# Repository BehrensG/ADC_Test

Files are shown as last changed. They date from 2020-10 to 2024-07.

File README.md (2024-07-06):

<h1> ADC_Test </h1>

PCB design to test the multislope ADC concept created by Jaromir Sukuba (https://github.com/jaromir-sukuba).

<h2> Design </h2>

The project features a 4-layer PCB designed in the Eurocard 3U format. The PCB operates on a 24V DC power supply. Communication is handled via Ethernet, utilizing a RAW TCP protocol with SCPI command format.
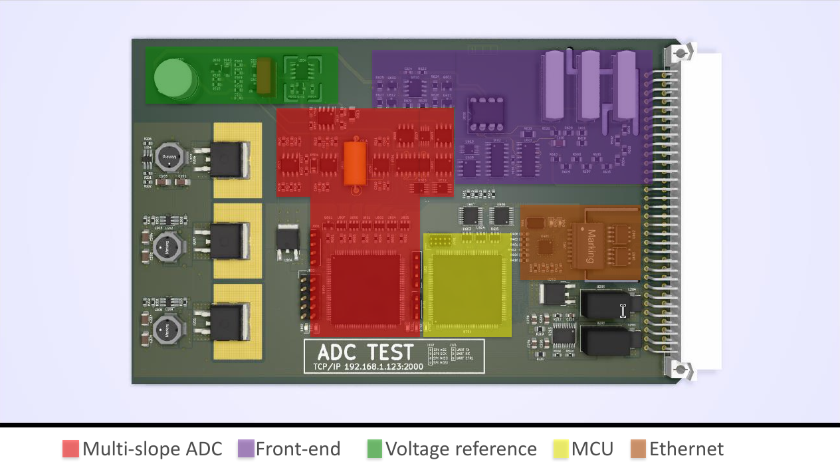
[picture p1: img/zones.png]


Key components include:
<ul>
    <li> <b>MCU</b>: STM32F765ZGT running FreeRTOS, developed with STM32CubeIDE.</li>
    <li> <b>FPGA</b>: ICE40HX4K-TQ144, with logic synthesis performed using IceStorm, and programmed in Verilog.</li>
    <li> <b>ADC</b> : Max voltage +/- 12V DC. 
            NPLC (Number of Power Line Cycles): 1, 2, 5,10 and 100.</li>
</ul>
The analog front end supports three bipolar ranges: 1V, 10V, and 100V DC.

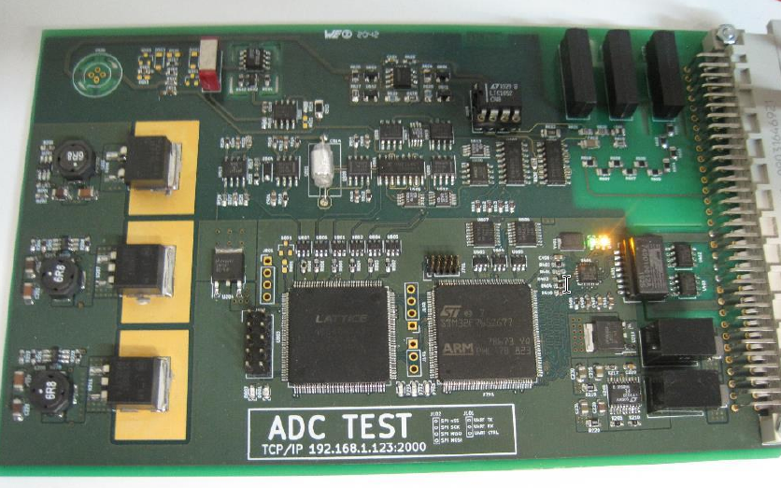
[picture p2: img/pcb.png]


<h2> Test </h2>

The PCB 3 measurement ranges where calibrated with a voltage calibrator (Inmel 7000). 

The calibrator voltage specification for voltage ranges are as follows: 

<table align="center">
    <tr>
        <th>Range</th>
        <th>Range setting</th>
        <th>Accuracy</th>
    </tr>
    <tr>
        <td>2V</td>
        <td>+/-2.1V</td>
        <td>+/-(30ppm S+ 5ppm R)</td>
    </tr>
    <tr>
        <td>20V</td>
        <td>+/-21V</td>
        <td>+/-(30ppm S + 5ppm R)</td>
    </tr>
    <tr>
        <td>200V</td>
        <td>+/-210V</td>
        <td>+/-(30ppm S + 5ppm R)</td>
    </tr>
</table>
<p align="center">S - set value, R - range rated value</p>

<h3> DMM with ADC comparison</h3>

<p>The Inmel 700 calibrator was used as the voltage source. DMM (34411A) results are used as reference values. DMM and ADC are setup for 100 NPLC, auto-zero once. Average from 150 samples.</p>

<p align="center"><b>Positive voltages</b></p>

<table align="center">
    <tr>
        <th>Range (V)</th>
        <th>Value (V)</th>
        <th>DMM (V)</th>
        <th>ADC (V)</th>
        <th>Error (%)</th>
    </tr>
    <tr>
        <td>1</td>
        <td>0.1</td>
        <td>0.100001</td>
        <td>0.100008</td>
        <td>0.0070</td>
    </tr>
    <tr>
        <td>1</td>
        <td>0.2</td>
        <td>0.200005</td>
        <td>0.200013</td>
        <td>0.0040</td>
    </tr>
    <tr>
        <td>1</td>
        <td>0.5</td>
        <td>0.500009</td>
        <td>0.500015</td>
        <td>0.0012</td>
    </tr>
    <tr>
        <td>1</td>
        <td>1</td>
        <td>1.000012</td>
        <td>1.000009</td>
        <td>0.0003</td>
    </tr>
    <tr>
        <td>10</td>
        <td>1</td>
        <td>1.00000</td>
        <td>1.00003</td>
        <td>0.0030</td>
    </tr>
    <tr>
        <td>10</td>
        <td>2</td>
        <td>2.00005</td>
        <td>2.00004</td>
        <td>0.0005</td>
    </tr>
    <tr>
        <td>10</td>
        <td>5</td>
        <td>5.00021</td>
        <td>5.00018</td>
        <td>0.0006</td>
    </tr>
    <tr>
        <td>10</td>
        <td>10</td>
        <td>10.0005</td>
        <td>10.0005</td>
        <td>0.0000</td>
    </tr>
    <tr>
        <td>100</td>
        <td>10</td>
        <td>10.0005</td>
        <td>9.99996</td>
        <td>0.0054</td>
    </tr>
    <tr>
        <td>100</td>
        <td>20</td>
        <td>20.0012</td>
        <td>20.0005</td>
        <td>0.0035</td>
    </tr>
    <tr>
        <td>100</td>
        <td>50</td>
        <td>50.0009</td>
        <td>50.0003</td>
        <td>0.0012</td>
    </tr>
    <tr>
        <td>100</td>
        <td>100</td>
        <td>100.0028</td>
        <td>100.0027</td>
        <td>0.0001</td>
    </tr>
</table>

<p align="center"><b>Negative voltages</b></p>

<table align="center">
    <tr>
        <th>Range (V)</th>
        <th>Value (V)</th>
        <th>DMM (V)</th>
        <th>ADC (V)</th>
        <th>Error (%)</th>
    </tr>
    <tr>
        <td>1</td>
        <td>-0.1</td>
        <td>-0.0999999</td>
        <td>-0.0999819</td>
        <td>0.0018</td>
    </tr>
    <tr>
        <td>1</td>
        <td>-0.2</td>
        <td>-0.199999</td>
        <td>-0.199976</td>
        <td>0.0115</td>
    </tr>
    <tr>
        <td>1</td>
        <td>-0.5</td>
        <td>-0.500002</td>
        <td>-0.499979</td>
        <td>0.0046</td>
    </tr>
    <tr>
        <td>1</td>
        <td>-1</td>
        <td>-1.00001</td>
        <td>-0.999967</td>
        <td>0.0043</td>
    </tr>
    <tr>
        <td>10</td>
        <td>-1</td>
        <td>-1.000020</td>
        <td>-0.999981</td>
        <td>0.0039</td>
    </tr>
    <tr>
        <td>10</td>
        <td>-2</td>
        <td>-2.00002</td>
        <td>-1.99998</td>
        <td>0.0020</td>
    </tr>
    <tr>
        <td>10</td>
        <td>-5</td>
        <td>-5.00014</td>
        <td>-5.00008</td>
        <td>0.0012</td>
    </tr>
    <tr>
        <td>10</td>
        <td>-10</td>
        <td>-10.0004</td>
        <td>-10.0003</td>
        <td>0.0010</td>
    </tr>
    <tr>
        <td>100</td>
        <td>-10</td>
        <td>-10.0004</td>
        <td>-10.0003</td>
        <td>0.0010</td>
    </tr>
    <tr>
        <td>100</td>
        <td>-20</td>
        <td>-20.0011</td>
        <td>-20.0009</td>
        <td>0.0010</td>
    </tr>
    <tr>
        <td>100</td>
        <td>-50</td>
        <td>-50.0007</td>
        <td>-49.9997</td>
        <td>0.0020</td>
    </tr>
    <tr>
        <td>100</td>
        <td>-100</td>
        <td>-100.003</td>
        <td>-100.001</td>
        <td>0.0020</td>
    </tr>
</table>

<h3> Measurements graphs</h3>

<p><b>NOTE</b> : DMM and PCB sampling was not synchronized.</p>

<p align="center"><b>Positive voltage samples</b></p>

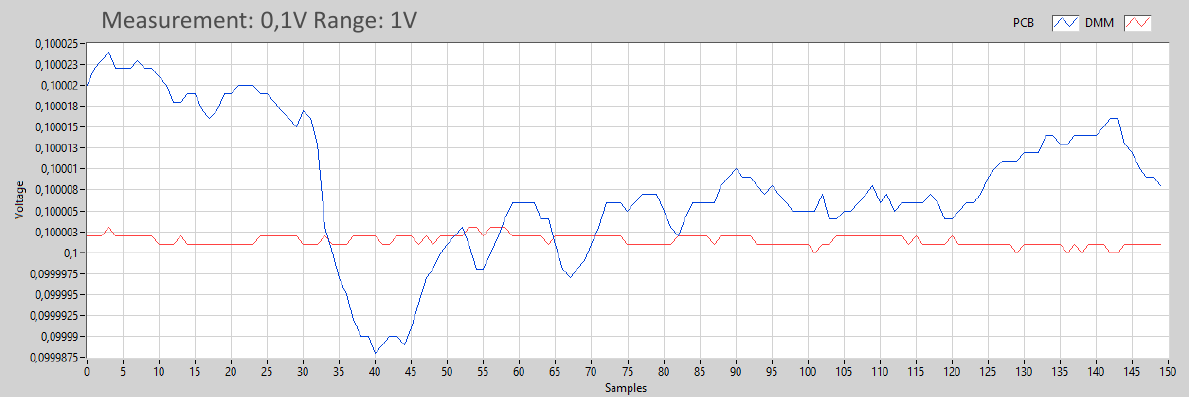
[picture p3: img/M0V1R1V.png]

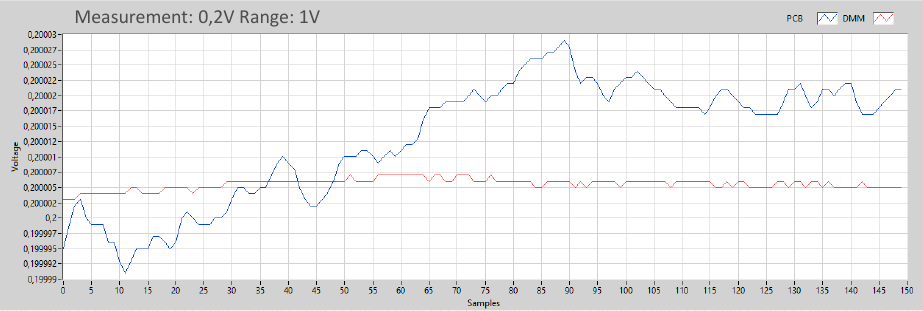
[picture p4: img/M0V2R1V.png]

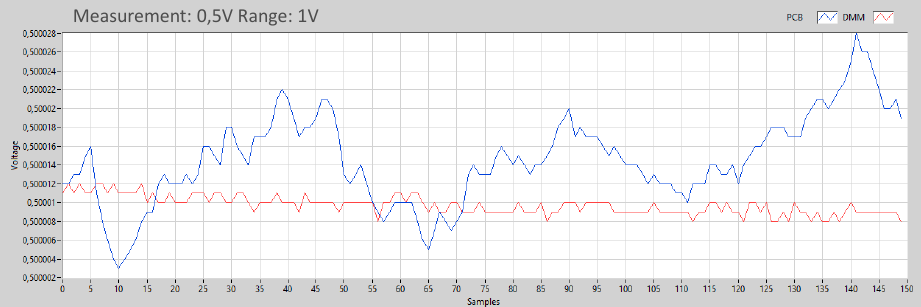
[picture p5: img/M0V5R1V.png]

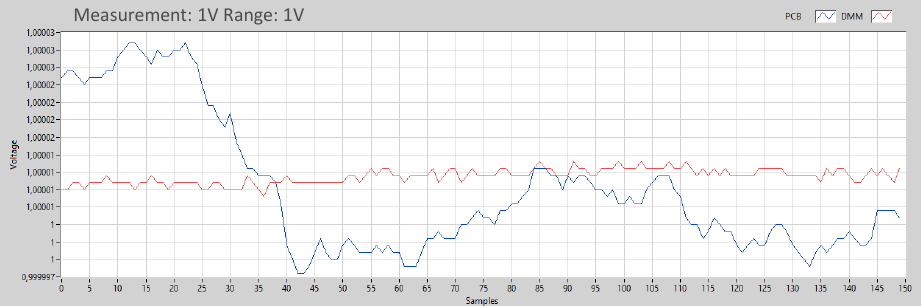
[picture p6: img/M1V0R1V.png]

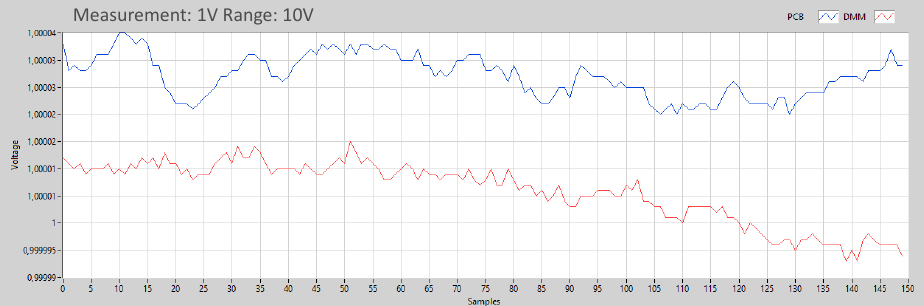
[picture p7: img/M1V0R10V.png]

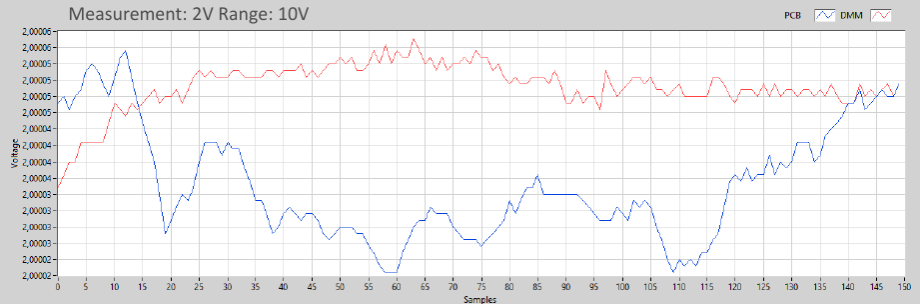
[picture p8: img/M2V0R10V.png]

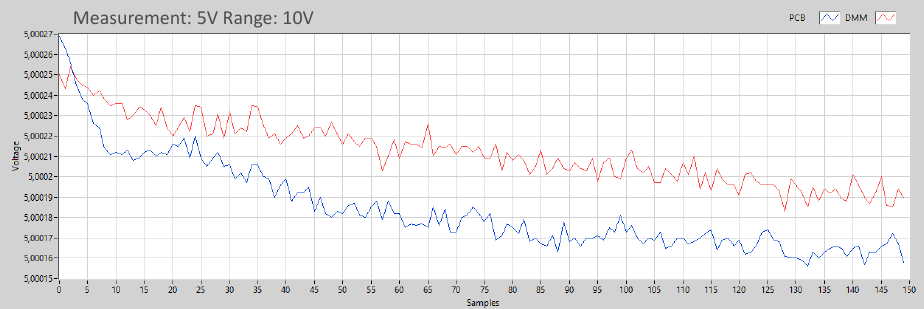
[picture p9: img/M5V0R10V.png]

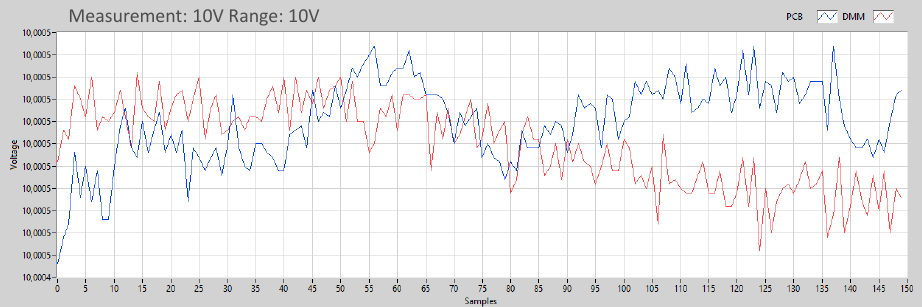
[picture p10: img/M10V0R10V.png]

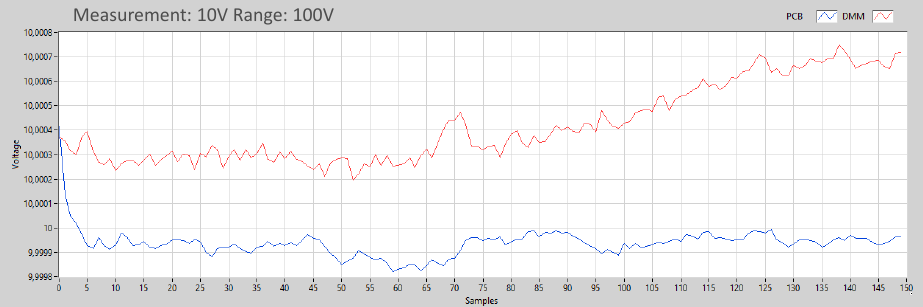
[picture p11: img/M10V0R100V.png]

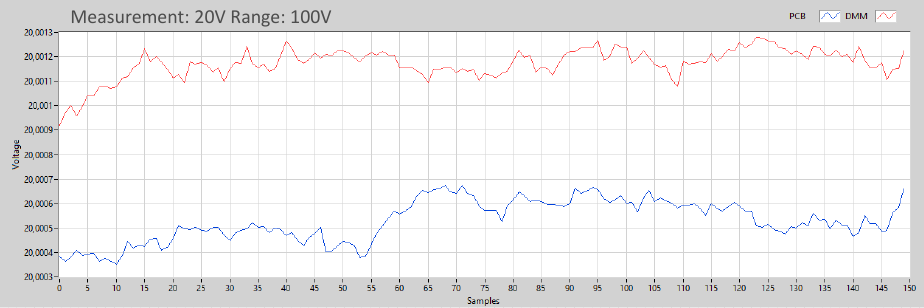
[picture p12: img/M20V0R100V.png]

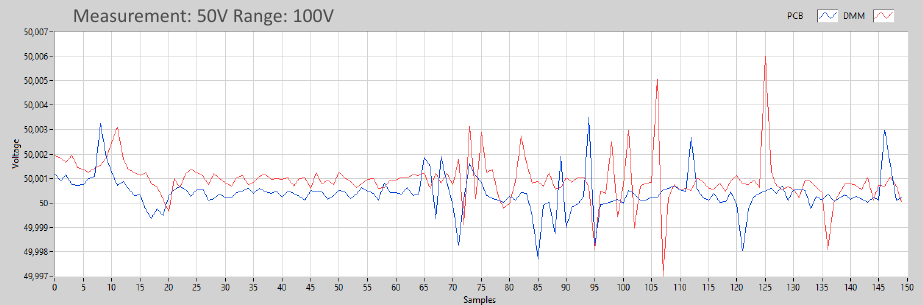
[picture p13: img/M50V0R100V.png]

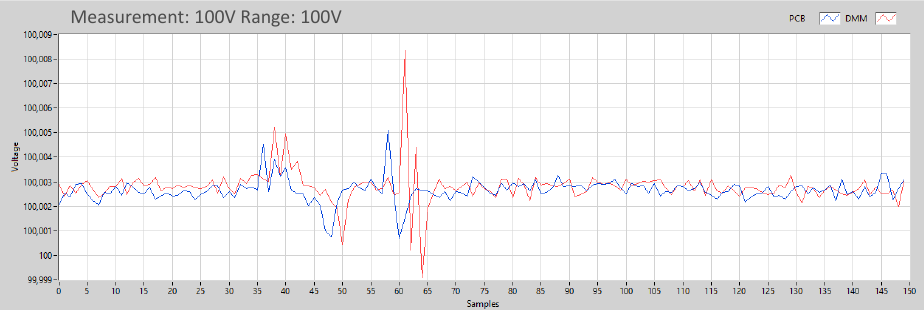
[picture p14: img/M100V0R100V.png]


<p align="center"><b>Negative voltage samples</b></p>

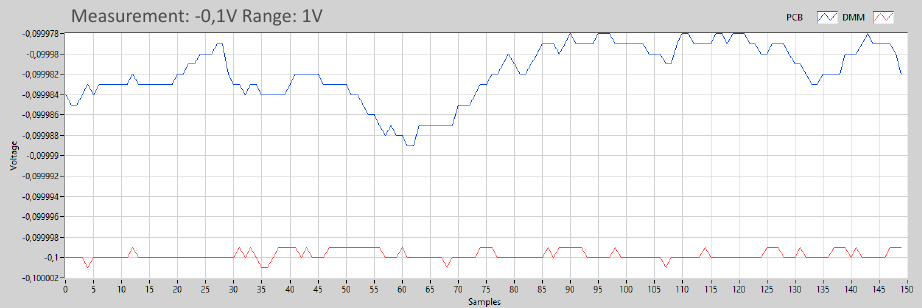
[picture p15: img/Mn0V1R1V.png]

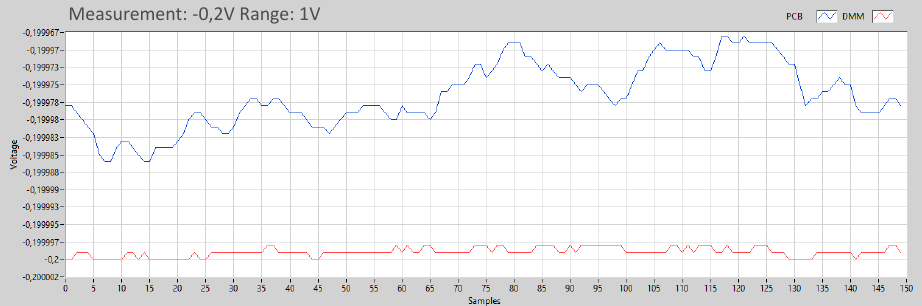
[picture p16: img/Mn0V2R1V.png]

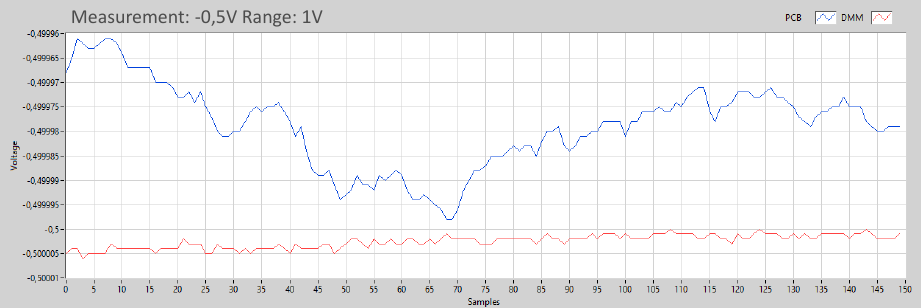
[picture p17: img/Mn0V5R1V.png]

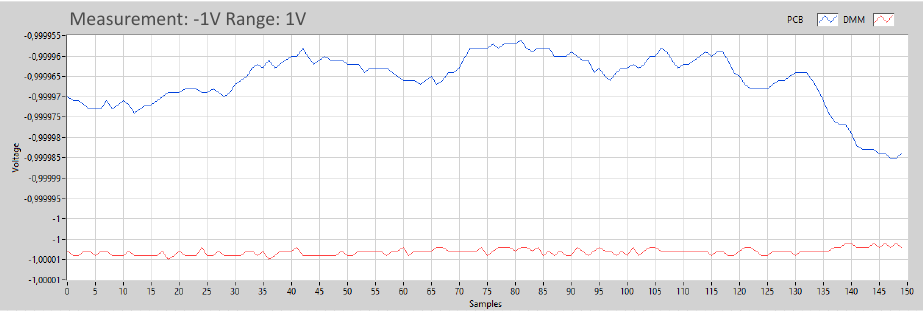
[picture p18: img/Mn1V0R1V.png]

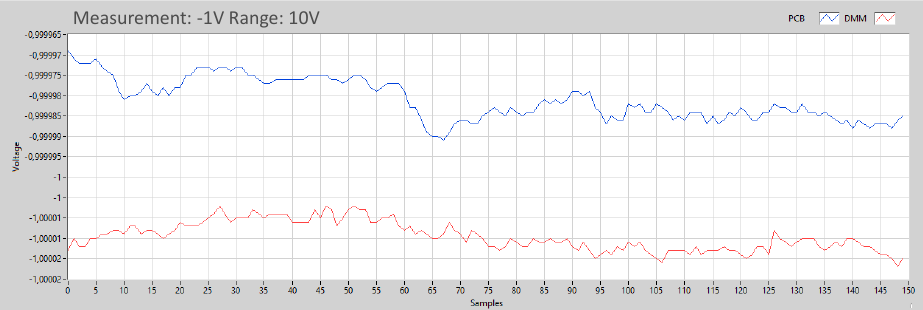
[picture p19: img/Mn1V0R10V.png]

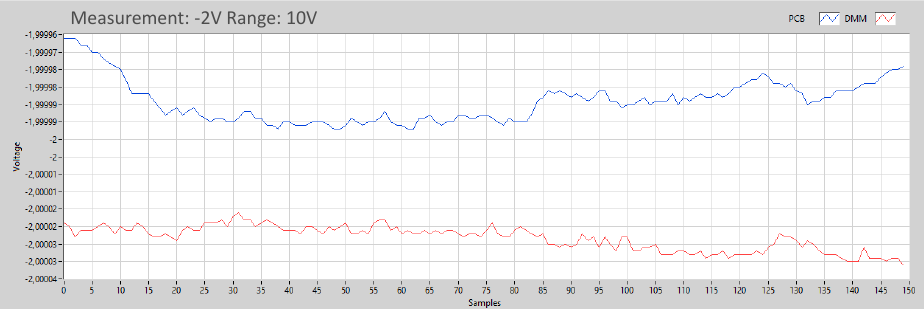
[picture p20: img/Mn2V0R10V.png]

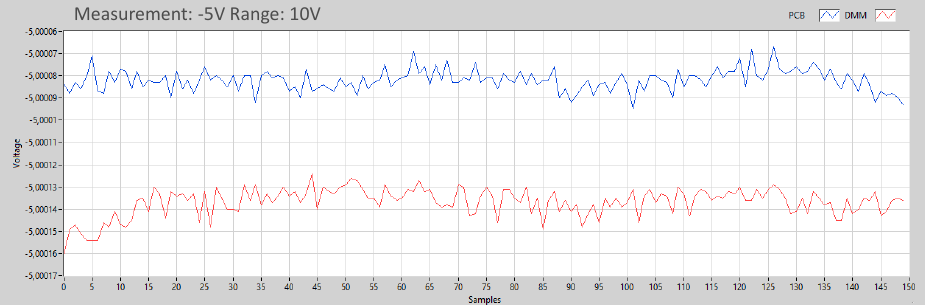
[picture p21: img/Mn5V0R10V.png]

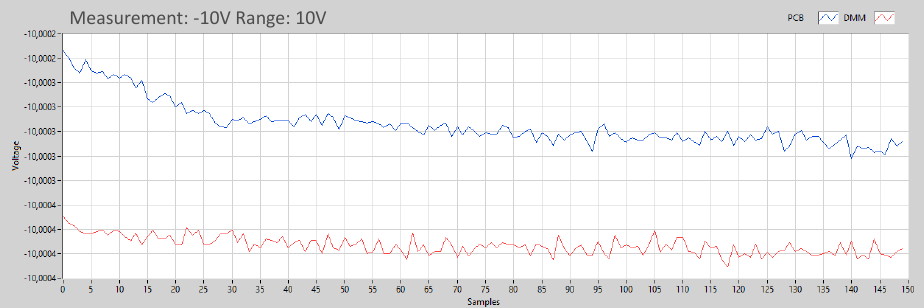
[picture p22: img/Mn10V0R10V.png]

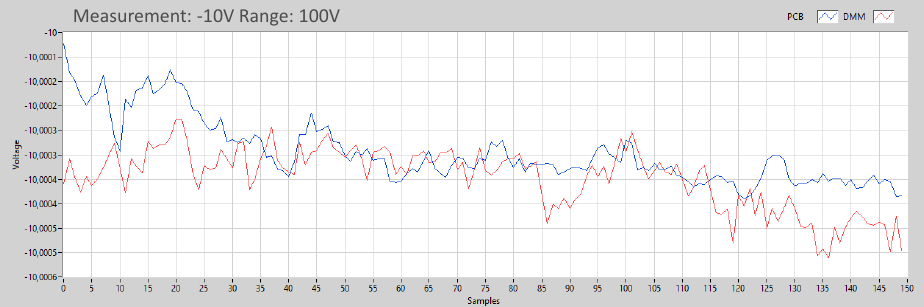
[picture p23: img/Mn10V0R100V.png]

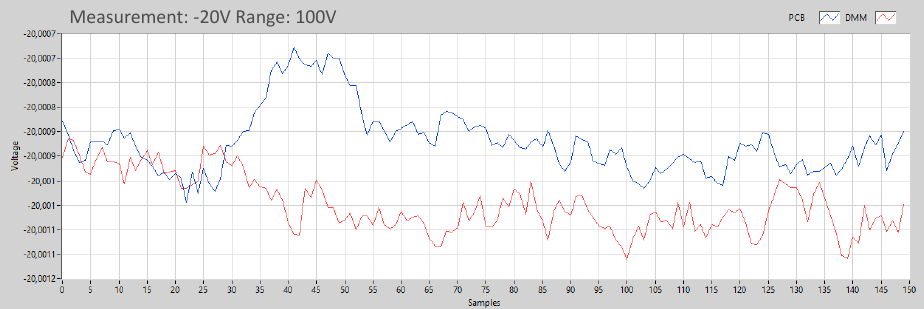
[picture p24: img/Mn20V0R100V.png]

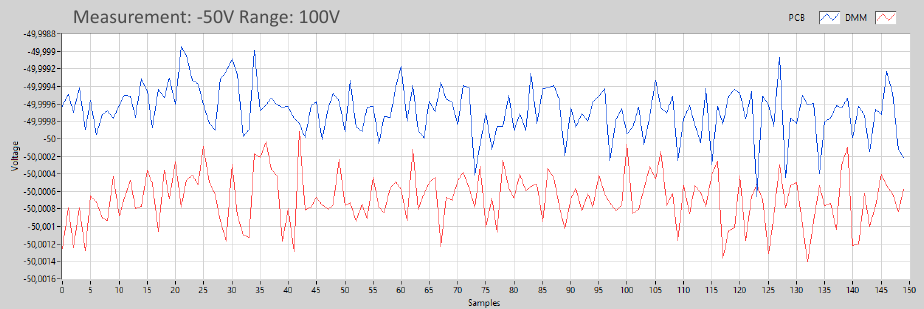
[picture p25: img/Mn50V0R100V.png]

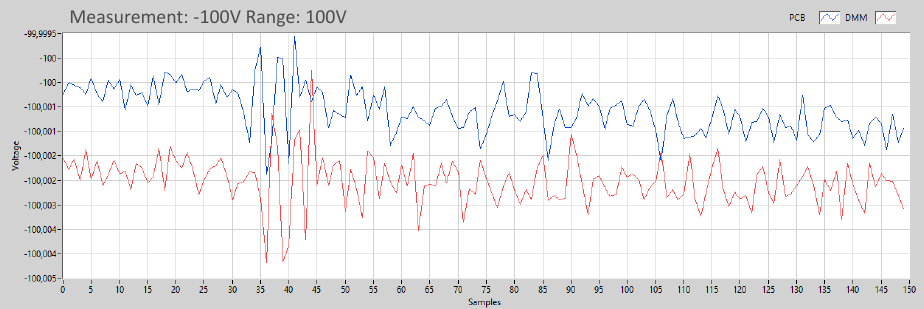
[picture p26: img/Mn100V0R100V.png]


<h2>Links</h2>

<ul>
    <li><a href="https://en.wikipedia.org/wiki/Integrating_ADC" target="_blank">Integrating ADC</a></li>
        <li><a href="https://patentimages.storage.googleapis.com/1c/fb/ba/970d5c758ec96f/US5321403.pdf" target="_blank">Multi-slope ADC patent</a></li>
        <li><a href="https://github.com/jaromir-sukuba/vm_mini" target="_blank">vm_mini</a></li>
        <li><a href="https://www.eevblog.com/forum/metrology/diy-6-5-digit-voltmeter/" target="_blank">DIY 6.5 digit voltmeter</a></li>
</ul>

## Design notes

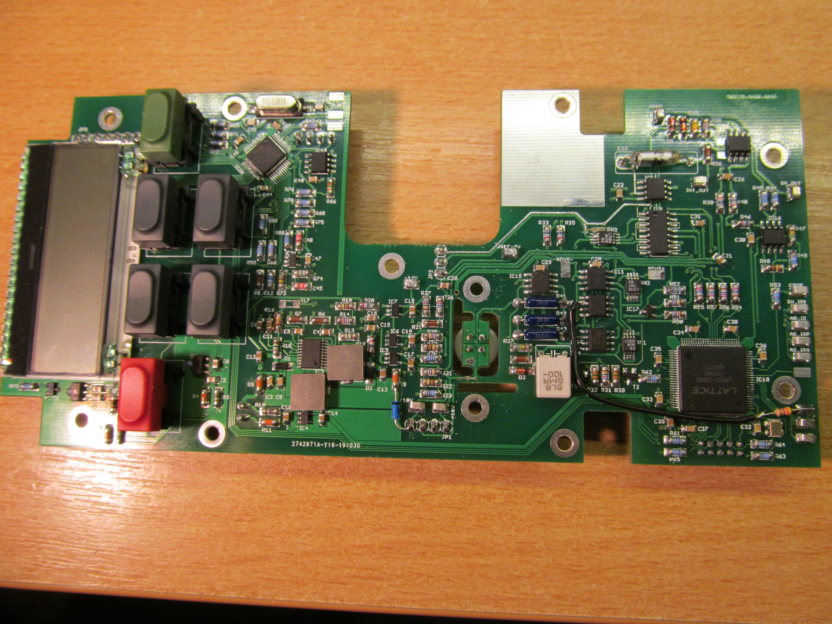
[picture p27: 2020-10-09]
doc/vm_mini-master/images/UoFq0qp.jpg

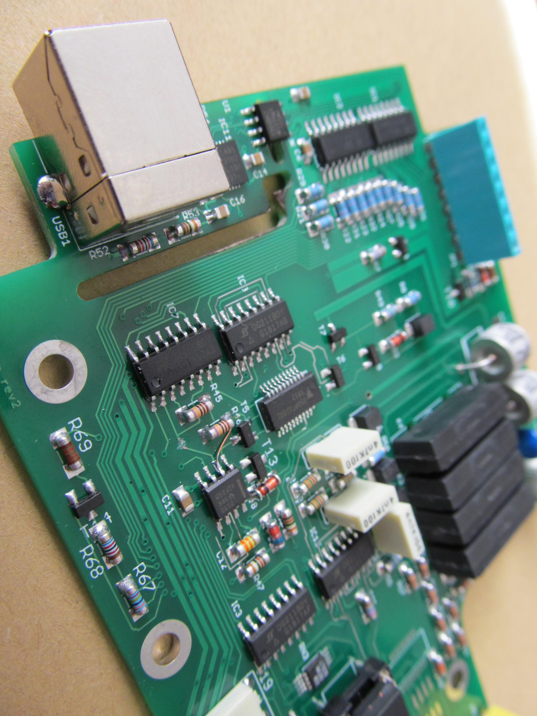
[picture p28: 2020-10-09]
doc/vm_mini-master/images/A4J0f3j.jpg

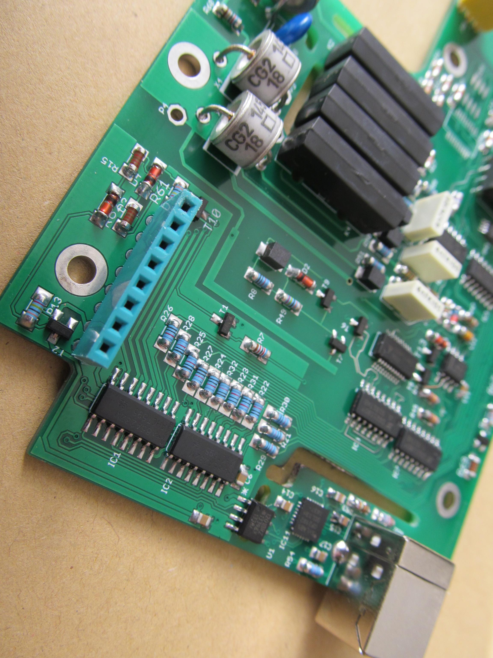
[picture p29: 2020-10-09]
doc/vm_mini-master/images/9xUZhGH.jpg

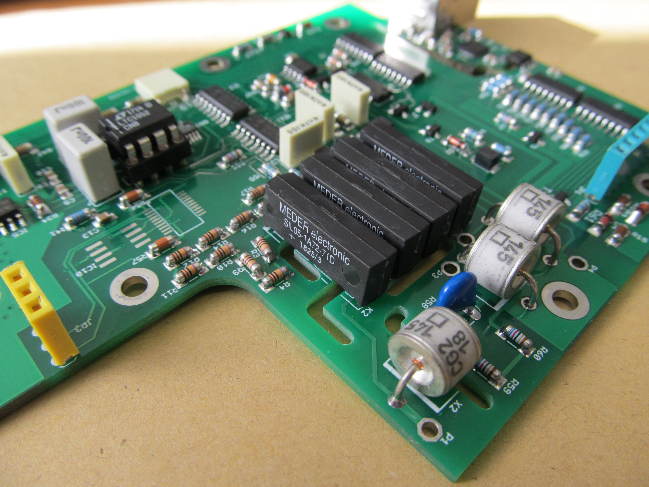
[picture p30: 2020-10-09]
doc/vm_mini-master/images/mZM4EhI.jpg

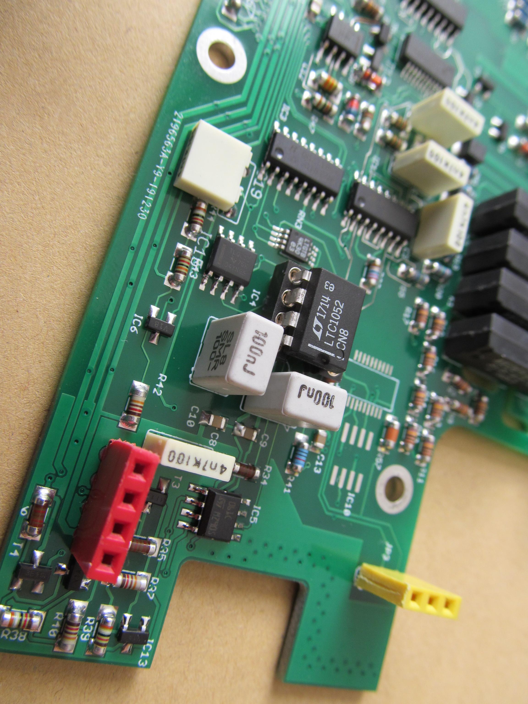
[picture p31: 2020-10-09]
doc/vm_mini-master/images/f6qNfNS.jpg

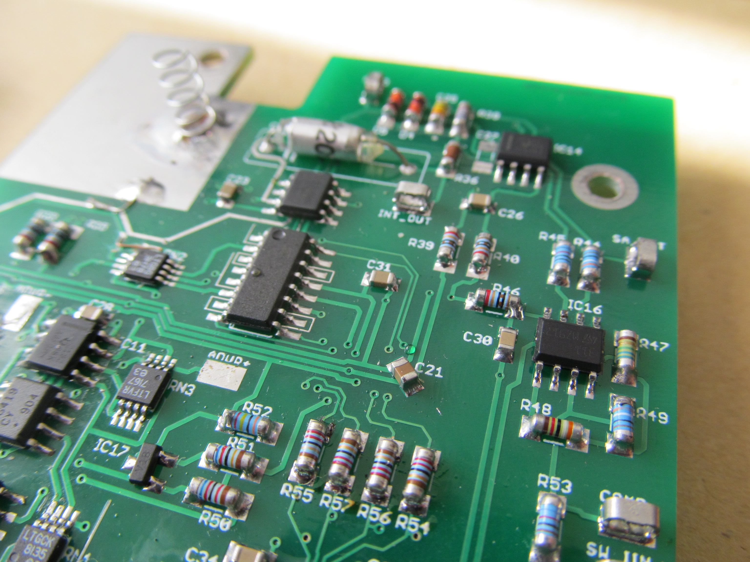
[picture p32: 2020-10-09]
doc/vm_mini-master/images/3wzWLv2.jpg

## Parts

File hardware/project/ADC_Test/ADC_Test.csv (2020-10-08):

Id | Designator | Package | Quantity | Designation | Supplier and ref
1 | K603,K602,K601 | HE360_x-5050462-8 | 3 | HE3621A0510
2 | D203,D202,D201 | D_SOD-128 | 3 | PMEG6010EP,115
3 | Y701 | NX3225GD | 1 | NX3225GD-8MHZ-STD-CRA-3
4 | Y401 | NX5032GA | 1 | NX5032GA-25.000M-LN-CD-1
5 | U809 | SOIC-8_5.23x5.23mm_P1.27mm | 1 | MT25QL128ABA1ESE
6 | U808 | Oscillator_SMD_Abracon_ASDMB-4Pin_2.5x2.0mm | 1 | ASDMB-100.000MHZ
7 | U807,U806,U805,U804,U802,U801,U605,U604,U603 | SOT-23-6 | 9 | SN74LVC1T45DBV
8 | U803 | TQFP-144_20x20mm_P0.5mm | 1 | ICE40HX4K-TQ144
9 | U702 | MSOP-8_3x3mm_P0.65mm | 1 | 24LC08B-E/MS
10 | U701 | TQFP-144_20x20mm_P0.5mm | 1 | STM32H743ZI/STM32F765ZGT6
11 | U613 | MSOP-8-1EP_3x3mm_P0.65mm_EP1.73x1.85mm_ThermalVias | 1 | LT5400-9k-1k
12 | U612,U611 | SOT-23 | 2 | TL431DBZ
13 | U610,U609 | SOIC-8_3.9x4.9mm_P1.27mm | 2 | AD711
14 | U608 | DIP-8_W7.62mm_Socket | 1 | LTC1052
15 | U607,U606 | TSSOP-16_4.4x5mm_P0.65mm | 2 | 74HCT595
16 | U602,U601,U501 | SOIC-16_3.9x9.9mm_P1.27mm | 3 | DG211B
17 | U512 | SOIC-8_3.9x4.9mm_P1.27mm | 1 | LM311
18 | U511 | MSOP-8-1EP_3x3mm_P0.65mm_EP1.73x1.85mm_ThermalVias | 1 | LT5400-10k-10k
19 | U510 | SOIC-8_3.9x4.9mm_P1.27mm | 1 | OPA192
20 | U509,U507 | SOIC-8_3.9x4.9mm_P1.27mm | 2 | OPA177
21 | U508 | SOIC-8_3.9x4.9mm_P1.27mm | 1 | OPA140
22 | U506 | MSOP-8-1EP_3x3mm_P0.65mm_EP1.73x1.85mm_ThermalVias | 1 | LT5400-5k-1k
23 | U505 | LMx99 | 1 | LM399H
24 | U504 | MSOP-8-1EP_3x3mm_P0.65mm_EP1.73x1.85mm_ThermalVias | 1 | LT5400-100k-100k
25 | U503 | SOIC-8_3.9x4.9mm_P1.27mm | 1 | DG419xY
26 | U502 | SOIC-8_3.9x4.9mm_P1.27mm | 1 | OPA2192
27 | U403,U402 | SO8E | 2 | LC03-3.3
28 | U401 | QFN-24-1EP_4x4mm_P0.5mm_EP2.6x2.6mm_ThermalVias | 1 | LAN8742A
29 | U211,U207 | TO-263-2 | 2 | LM337_TO263
30 | U210 | TO-252-2 | 1 | LM1117DTX-3.3/NOPB
31 | U209,U202,U201 | TSOT-23-6_HandSoldering | 3 | LT8330_S6
32 | U208 | TSR1 | 1 | TSR1-2450
33 | U206 | TO-263-2 | 1 | LM317_TO-263
34 | U205 | ETSSOP-20-1EP_4.4x6.5mm_P0.65mm_EP3x4.2mm | 1 | LT3030
35 | U204 | TO-252-2 | 1 | LM1117DTX-5.0/NOPB
36 | U203 | TSR1 | 1 | TSR1-2490
37 | TP503,TP502,TP501 | TestPoint_Loop_D2.60mm_Drill1.6mm_Beaded | 3 | TestPoint
38 | R820,R819,R818,R815,R814,R813,R706,R705 | R_0603_1608Metric_Pad1.05x0.95mm_HandSolder | 8 | 4k7
39 | R817,R810,R220,R219 | R_0603_1608Metric_Pad1.05x0.95mm_HandSolder | 4 | 100
40 | R816 | R_0603_1608Metric_Pad1.05x0.95mm_HandSolder | 1 | OPT
41 | R812,R811 | R_0603_1608Metric_Pad1.05x0.95mm_HandSolder | 2 | 22
42 | R809 | R_0603_1608Metric_Pad1.05x0.95mm_HandSolder | 1 | 6k2
43 | R808,R807,R801 | R_0603_1608Metric_Pad1.05x0.95mm_HandSolder | 3 | 1k
44 | R806,R805,R804,R803,R802 | R_0603_1608Metric_Pad1.05x0.95mm_HandSolder | 5 | 150
45 | R708,R707,R701,R411,R409,R408,R407,R406,R403,R201 | R_0603_1608Metric_Pad1.05x0.95mm_HandSolder | 10 | 10k
46 | R704,R702 | R_0603_1608Metric_Pad1.05x0.95mm_HandSolder | 2 | 680
47 | R703 | R_0603_1608Metric_Pad1.05x0.95mm_HandSolder | 1 | 560
48 | R630,R517 | R_0603_1608Metric_Pad1.05x0.95mm_HandSolder | 2 | 620/.05%
49 | R629,R626 | R_0805_2012Metric_Pad1.15x1.40mm_HandSolder | 2 | 93k
50 | R628,R627 | R_0805_2012Metric_Pad1.15x1.40mm_HandSolder | 2 | 39k
51 | R625,R624 | R_0805_2012Metric_Pad1.15x1.40mm_HandSolder | 2 | 12k
52 | R623,R509 | R_0603_1608Metric_Pad1.05x0.95mm_HandSolder | 2 | 12k/.05%
53 | R622 | R_1206_3216Metric_Pad1.42x1.75mm_HandSolder | 1 | 22/.1%
54 | R621,R620 | R_0805_2012Metric_Pad1.15x1.40mm_HandSolder | 2 | 240k
55 | R619 | R_0805_2012Metric_Pad1.15x1.40mm_HandSolder | 1 | 620
56 | R618,R617,R616,R615,R614,R613,R612,R611 | R_0603_1608Metric_Pad1.05x0.95mm_HandSolder | 8 | 620
57 | R610,R609,R608,R607,R606,R605,R604,R603,R602,R601 | R_1206_3216Metric_Pad1.42x1.75mm_HandSolder | 10 | 1M
58 | R522,R518 | R_0603_1608Metric_Pad1.05x0.95mm_HandSolder | 2 | 3k9/.05%
59 | R521 | R_0603_1608Metric_Pad1.05x0.95mm_HandSolder | 1 | 39k/.05%
60 | R520,R505 | R_0603_1608Metric_Pad1.05x0.95mm_HandSolder | 2 | 62/.1%
61 | R519,R514,R513,R507,R506 | R_0603_1608Metric_Pad1.05x0.95mm_HandSolder | 5 | 10
62 | R516 | R_0603_1608Metric_Pad1.05x0.95mm_HandSolder | 1 | 0
63 | R515 | R_0603_1608Metric_Pad1.05x0.95mm_HandSolder | 1 | 400/.1%
64 | R512 | R_0603_1608Metric_Pad1.05x0.95mm_HandSolder | 1 | 62k6/.1%
65 | R511 | R_0603_1608Metric_Pad1.05x0.95mm_HandSolder | 1 | 3k01/.1%
66 | R510 | R_0603_1608Metric_Pad1.05x0.95mm_HandSolder | 1 | 1k96/.1%
67 | R508 | R_1206_3216Metric_Pad1.42x1.75mm_HandSolder | 1 | 6k95/.05%
68 | R504 | R_0603_1608Metric_Pad1.05x0.95mm_HandSolder | 1 | 12k
69 | R503,R501 | R_0603_1608Metric_Pad1.05x0.95mm_HandSolder | 2 | 120k
70 | R502 | R_0603_1608Metric_Pad1.05x0.95mm_HandSolder | 1 | 620k
71 | R421,R420 | R_0603_1608Metric_Pad1.05x0.95mm_HandSolder | 2 | 75/1%
72 | R419 | R_1206_3216Metric_Pad1.42x1.75mm_HandSolder | 1 | 1M/1kV
73 | R418,R417,R416,R415 | R_0603_1608Metric_Pad1.05x0.95mm_HandSolder | 4 | 49R9
74 | R414,R413 | R_0603_1608Metric_Pad1.05x0.95mm_HandSolder | 2 | 270
75 | R412 | R_0603_1608Metric_Pad1.05x0.95mm_HandSolder | 1 | 12k1
76 | R410 | R_0603_1608Metric_Pad1.05x0.95mm_HandSolder | 1 | 1k5
77 | R405,R404,R402,R401 | R_0603_1608Metric_Pad1.05x0.95mm_HandSolder | 4 | 33
78 | R228,R216,R215 | R_0603_1608Metric_Pad1.05x0.95mm_HandSolder | 3 | 120
79 | R227 | R_0603_1608Metric_Pad1.05x0.95mm_HandSolder | 1 | 1k23
80 | R226 | R_0603_1608Metric_Pad1.05x0.95mm_HandSolder | 1 | 46k4
81 | R225,R223,R212,R210,R208,R207,R206,R204,R202 | R_0603_1608Metric_Pad1.05x0.95mm_HandSolder | 9 | 1M
82 | R224,R205,R203 | R_0603_1608Metric_Pad1.05x0.95mm_HandSolder | 3 | 287k
83 | R222,R221 | R_0805_2012Metric_Pad1.15x1.40mm_HandSolder | 2 | 0R1
84 | R218 | R_0603_1608Metric_Pad1.05x0.95mm_HandSolder | 1 | 210k
85 | R217 | R_0603_1608Metric_Pad1.05x0.95mm_HandSolder | 1 | 357k
86 | R214,R213 | R_0603_1608Metric_Pad1.05x0.95mm_HandSolder | 2 | 1k6
87 | R211 | R_0603_1608Metric_Pad1.05x0.95mm_HandSolder | 1 | 39k3
88 | R209 | R_0603_1608Metric_Pad1.05x0.95mm_HandSolder | 1 | 82k5
89 | Q801,Q602 | SOT-323_SC-70 | 2 | BC857W
90 | Q601,Q501,Q201 | SOT-323_SC-70 | 3 | BC847W
91 | L601 | R_0805_2012Metric_Pad1.15x1.40mm_HandSolder | 1 | L0805R100MPWRT
92 | L401 | 749010012A | 1 | 749010012A
93 | L205,L203,L202 | 74489440068 | 3 | 74489440068
94 | L204,L201 | TCK-141 | 2 | TCK-141
95 | J802 | PinHeader_2x05_P2.54mm_Vertical | 1 | Conn_02x05
96 | J801,J103 | PinHeader_1x04_P2.54mm_Vertical | 2 | Conn_01x04_Male
97 | J702 | PinHeader_2x05_P1.27mm_Vertical | 1 | 20021111-00010T4LF
98 | J701 | PinHeader_1x02_P2.54mm_Vertical | 1 | Conn_02x01
99 | J301 | Socket_DIN41612-CaseC1-AC-Male-64Pin-2rows | 1 | C64AC
100 | J102 | PinHeader_1x02_P2.54mm_Vertical | 1 | Conn_01x02_Male
101 | J101 | 36107406S | 1 | RF_Shield_One_Piece
102 | FB701,FB401 | L_0805_2012Metric_Pad1.15x1.40mm_HandSolder | 2 | 742792031
103 | D803 | D_SOD-523 | 1 | CDBU0520
104 | D802,D701 | LED_0603_1608Metric_Pad1.05x0.95mm_HandSolder | 2 | RED
105 | D801,D702,D402 | LED_0603_1608Metric_Pad1.05x0.95mm_HandSolder | 3 | GREEN
106 | D703 | LED_0603_1608Metric_Pad1.05x0.95mm_HandSolder | 1 | BLUE
107 | D503,D502,D501 | D_SOD-123 | 3 | BAV21W
108 | D401 | LED_0603_1608Metric_Pad1.05x0.95mm_HandSolder | 1 | YELLOW
109 | C832,C830,C828,C827,C826,C825,C824,C823,C822,C821,C820,C819,C818,C817,C816,C815,C814,C813,C812,C811,C810,C809,C808,C807,C806,C805,C804,C803,C802,C801,C721,C719,C718,C717,C716,C715,C714,C713,C712,C710,C708,C705,C703,C702,C701,C624,C623,C622,C621,C620,C619,C618,C617,C616,C615,C614,C613,C612,C611,C609,C608,C607,C606,C605,C604,C603,C602,C601,C524,C523,C522,C521,C520,C519,C518,C516,C514,C513,C512,C511,C510,C507,C506,C505,C504,C503,C502,C501,C412,C411,C410,C409,C408,C405,C402,C238,C237 | C_0603_1608Metric_Pad1.05x0.95mm_HandSolder | 97 | 100n
110 | C831,C829,C232,C231,C226,C213 | C_0805_2012Metric_Pad1.15x1.40mm_HandSolder | 6 | 10u
111 | C720,C711,C407,C406,C236,C234,C233,C209,C208 | C_0603_1608Metric_Pad1.05x0.95mm_HandSolder | 9 | 1u
112 | C709,C707 | C_0805_2012Metric_Pad1.15x1.40mm_HandSolder | 2 | 2u2
113 | C706,C704,C404,C401 | C_0603_1608Metric_Pad1.05x0.95mm_HandSolder | 4 | 8p
114 | C626,C625 | C_0603_1608Metric_Pad1.05x0.95mm_HandSolder | 2 | 4n7
115 | C610 | C_1206_3216Metric_Pad1.42x1.75mm_HandSolder | 1 | 4n7
116 | C517 | C_0603_1608Metric_Pad1.05x0.95mm_HandSolder | 1 | DNP
117 | C515 | C_0603_1608Metric_Pad1.05x0.95mm_HandSolder | 1 | 33p
118 | C509 | C_0603_1608Metric_Pad1.05x0.95mm_HandSolder | 1 | 2n2/SMD
119 | C508 | C_Axial_L12.0mm_D6.5mm_P15.00mm_Horizontal | 1 | 23PS222
120 | C414,C413 | C_1206_3216Metric_Pad1.42x1.75mm_HandSolder | 2 | 1n/1kV
121 | C403 | C_0603_1608Metric_Pad1.05x0.95mm_HandSolder | 1 | 470p
122 | C246,C245,C244,C230,C224,C223,C220,C219,C218,C217,C204,C203 | C_1206_3216Metric_Pad1.42x1.75mm_HandSolder | 12 | 4u7/50V
123 | C243,C216,C215 | C_0603_1608Metric_Pad1.05x0.95mm_HandSolder | 3 | 4p7
124 | C242,C214 | C_1206_3216Metric_Pad1.42x1.75mm_HandSolder | 2 | 47u/16V
125 | C241,C240,C222,C221 | C_0603_1608Metric_Pad1.05x0.95mm_HandSolder | 4 | 10n
126 | C239,C211,C210 | C_1206_3216Metric_Pad1.42x1.75mm_HandSolder | 3 | 1u/HC
127 | C235,C212 | C_1206_3216Metric_Pad1.42x1.75mm_HandSolder | 2 | 10u/16V
128 | C229,C228,C225,C207,C205,C202,C201 | C_1206_3216Metric_Pad1.42x1.75mm_HandSolder | 7 | 10u/50V
129 | C227 | C_0805_2012Metric_Pad1.15x1.40mm_HandSolder | 1 | 4u7
130 | C206 | C_0603_1608Metric_Pad1.05x0.95mm_HandSolder | 1 | 10p

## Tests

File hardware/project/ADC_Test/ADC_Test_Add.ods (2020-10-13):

R_0603_1608Metric_Pad1.05x0.95mm_HandSolder | 1 | 3k01/.1%
SOIC-8_3.9x4.9mm_P1.27mm | 1 | LT1021-7
SOT-23 | 2 | MMBTA55
D_SOD-523 | 5 | BZT585B15TQ-13
R_0603_1608Metric_Pad1.05x0.95mm_HandSolder | 4 | 4k7/.1%
R_0603_1608Metric_Pad1.05x0.95mm_HandSolder | 10 | 0
 | 1 | 9012
D_SOD-123 | 1 | 1N4148W
 |  | 10p
R_0603_1608Metric_Pad1.05x0.95mm_HandSolder |  | 10k
SOT-23 |  | BC847
 | 20 | 5050462-8

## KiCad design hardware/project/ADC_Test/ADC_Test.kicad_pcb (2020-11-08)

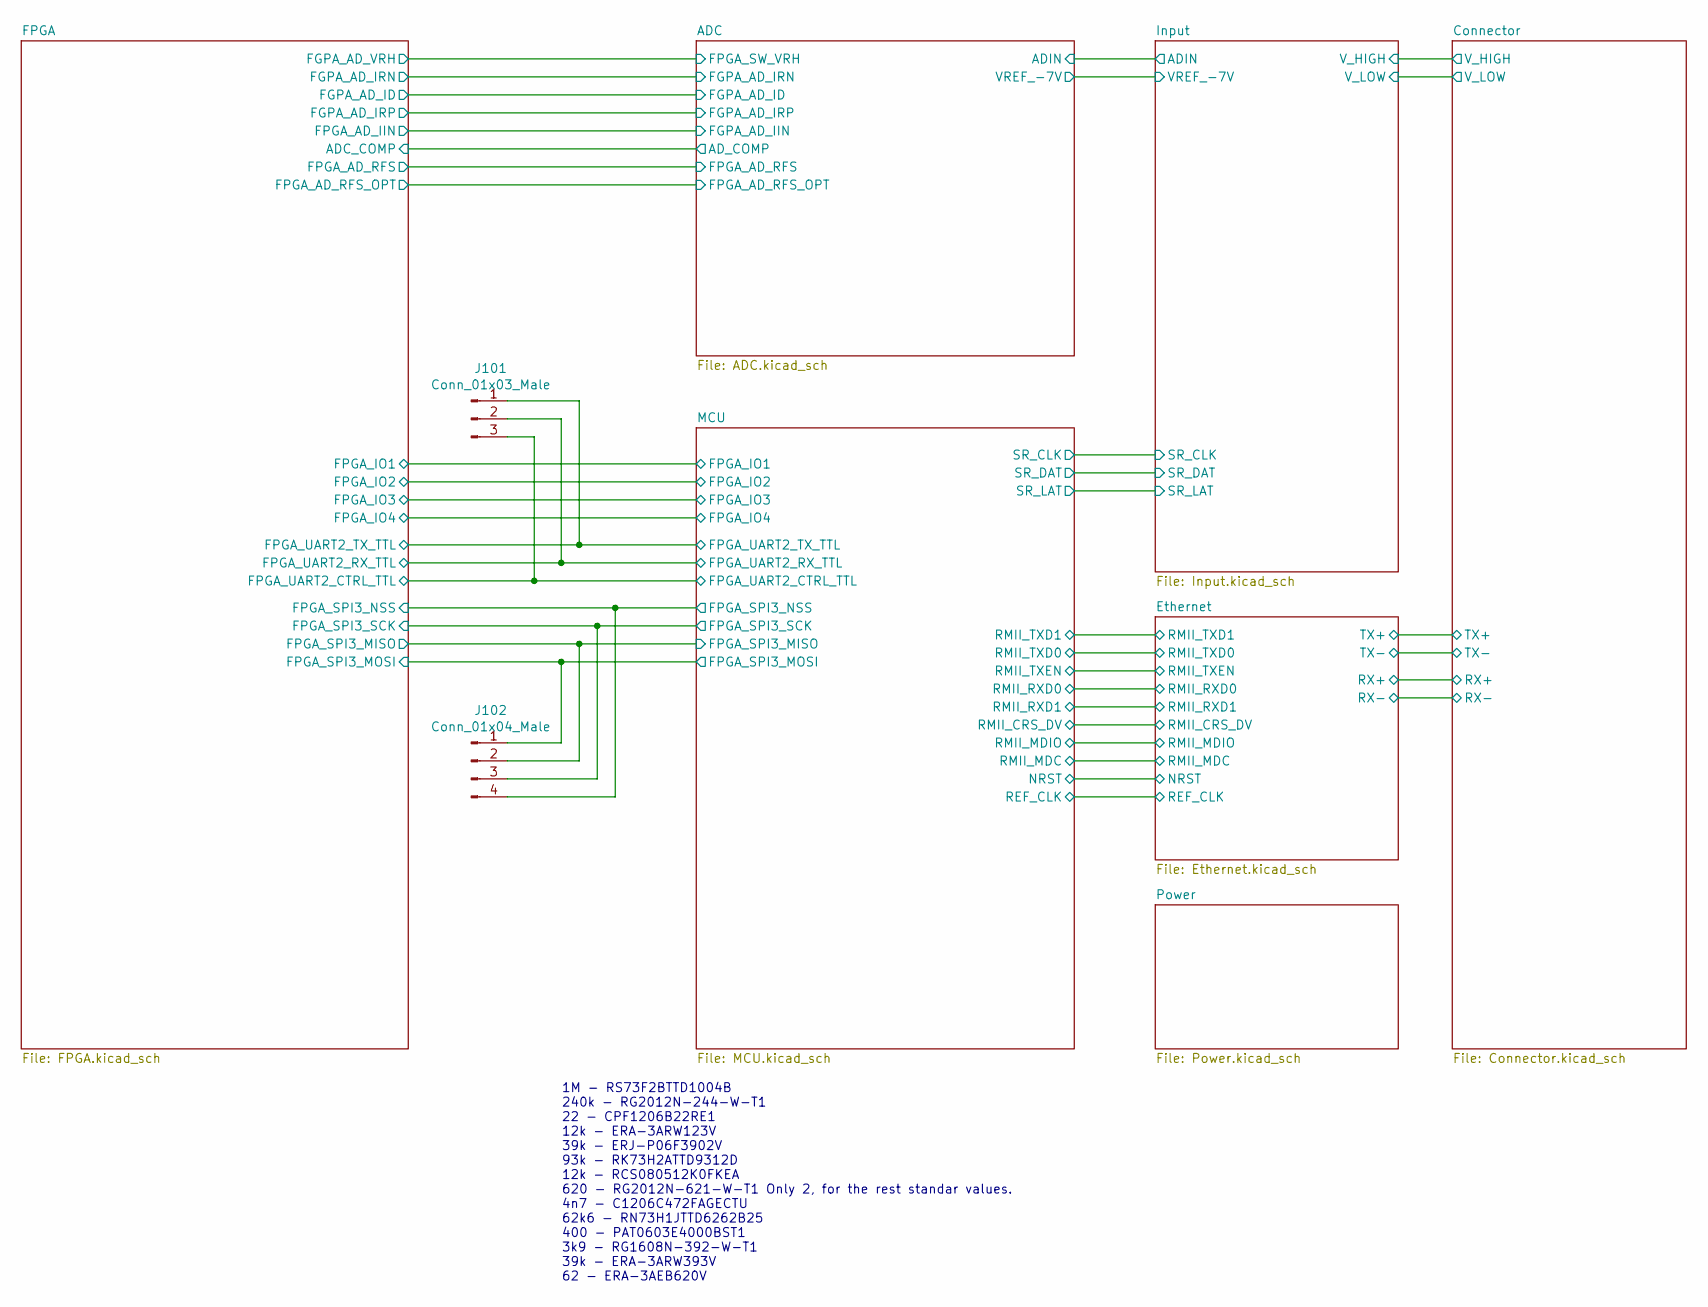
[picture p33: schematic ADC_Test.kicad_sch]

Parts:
J101: Conn_01x03_Male; PinHeader_1x03_P2.54mm_Vertical
J102: Conn_01x04_Male; PinHeader_1x04_P2.54mm_Vertical

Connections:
/FPGA/FPGA_SPI3_MISO: J102.2; also elsewhere on the board
/FPGA/FPGA_SPI3_MOSI: J102.1; also elsewhere on the board
/FPGA/FPGA_SPI3_NSS: J102.4; also elsewhere on the board
/FPGA/FPGA_SPI3_SCK: J102.3; also elsewhere on the board
/FPGA/FPGA_UART2_CTRL_TTL: J101.3; also elsewhere on the board
/FPGA/FPGA_UART2_RX_TTL: J101.2; also elsewhere on the board
/FPGA/FPGA_UART2_TX_TTL: J101.1; also elsewhere on the board

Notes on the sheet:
1M - RS73F2BTTD1004B 240k - RG2012N-244-W-T1 22 - CPF1206B22RE1 12k - ERA-3ARW123V 39k - ERJ-P06F3902V 93k - RK73H2ATTD9312D 12k - RCS080512K0FKEA 620 - RG2012N-621-W-T1 Only 2, for the rest standar values. 4n7 - C1206C472FAGECTU 62k6 - RN73H1JTTD6262B25 400 - PAT0603E4000BST1 3k9 - RG1608N-392-W-T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

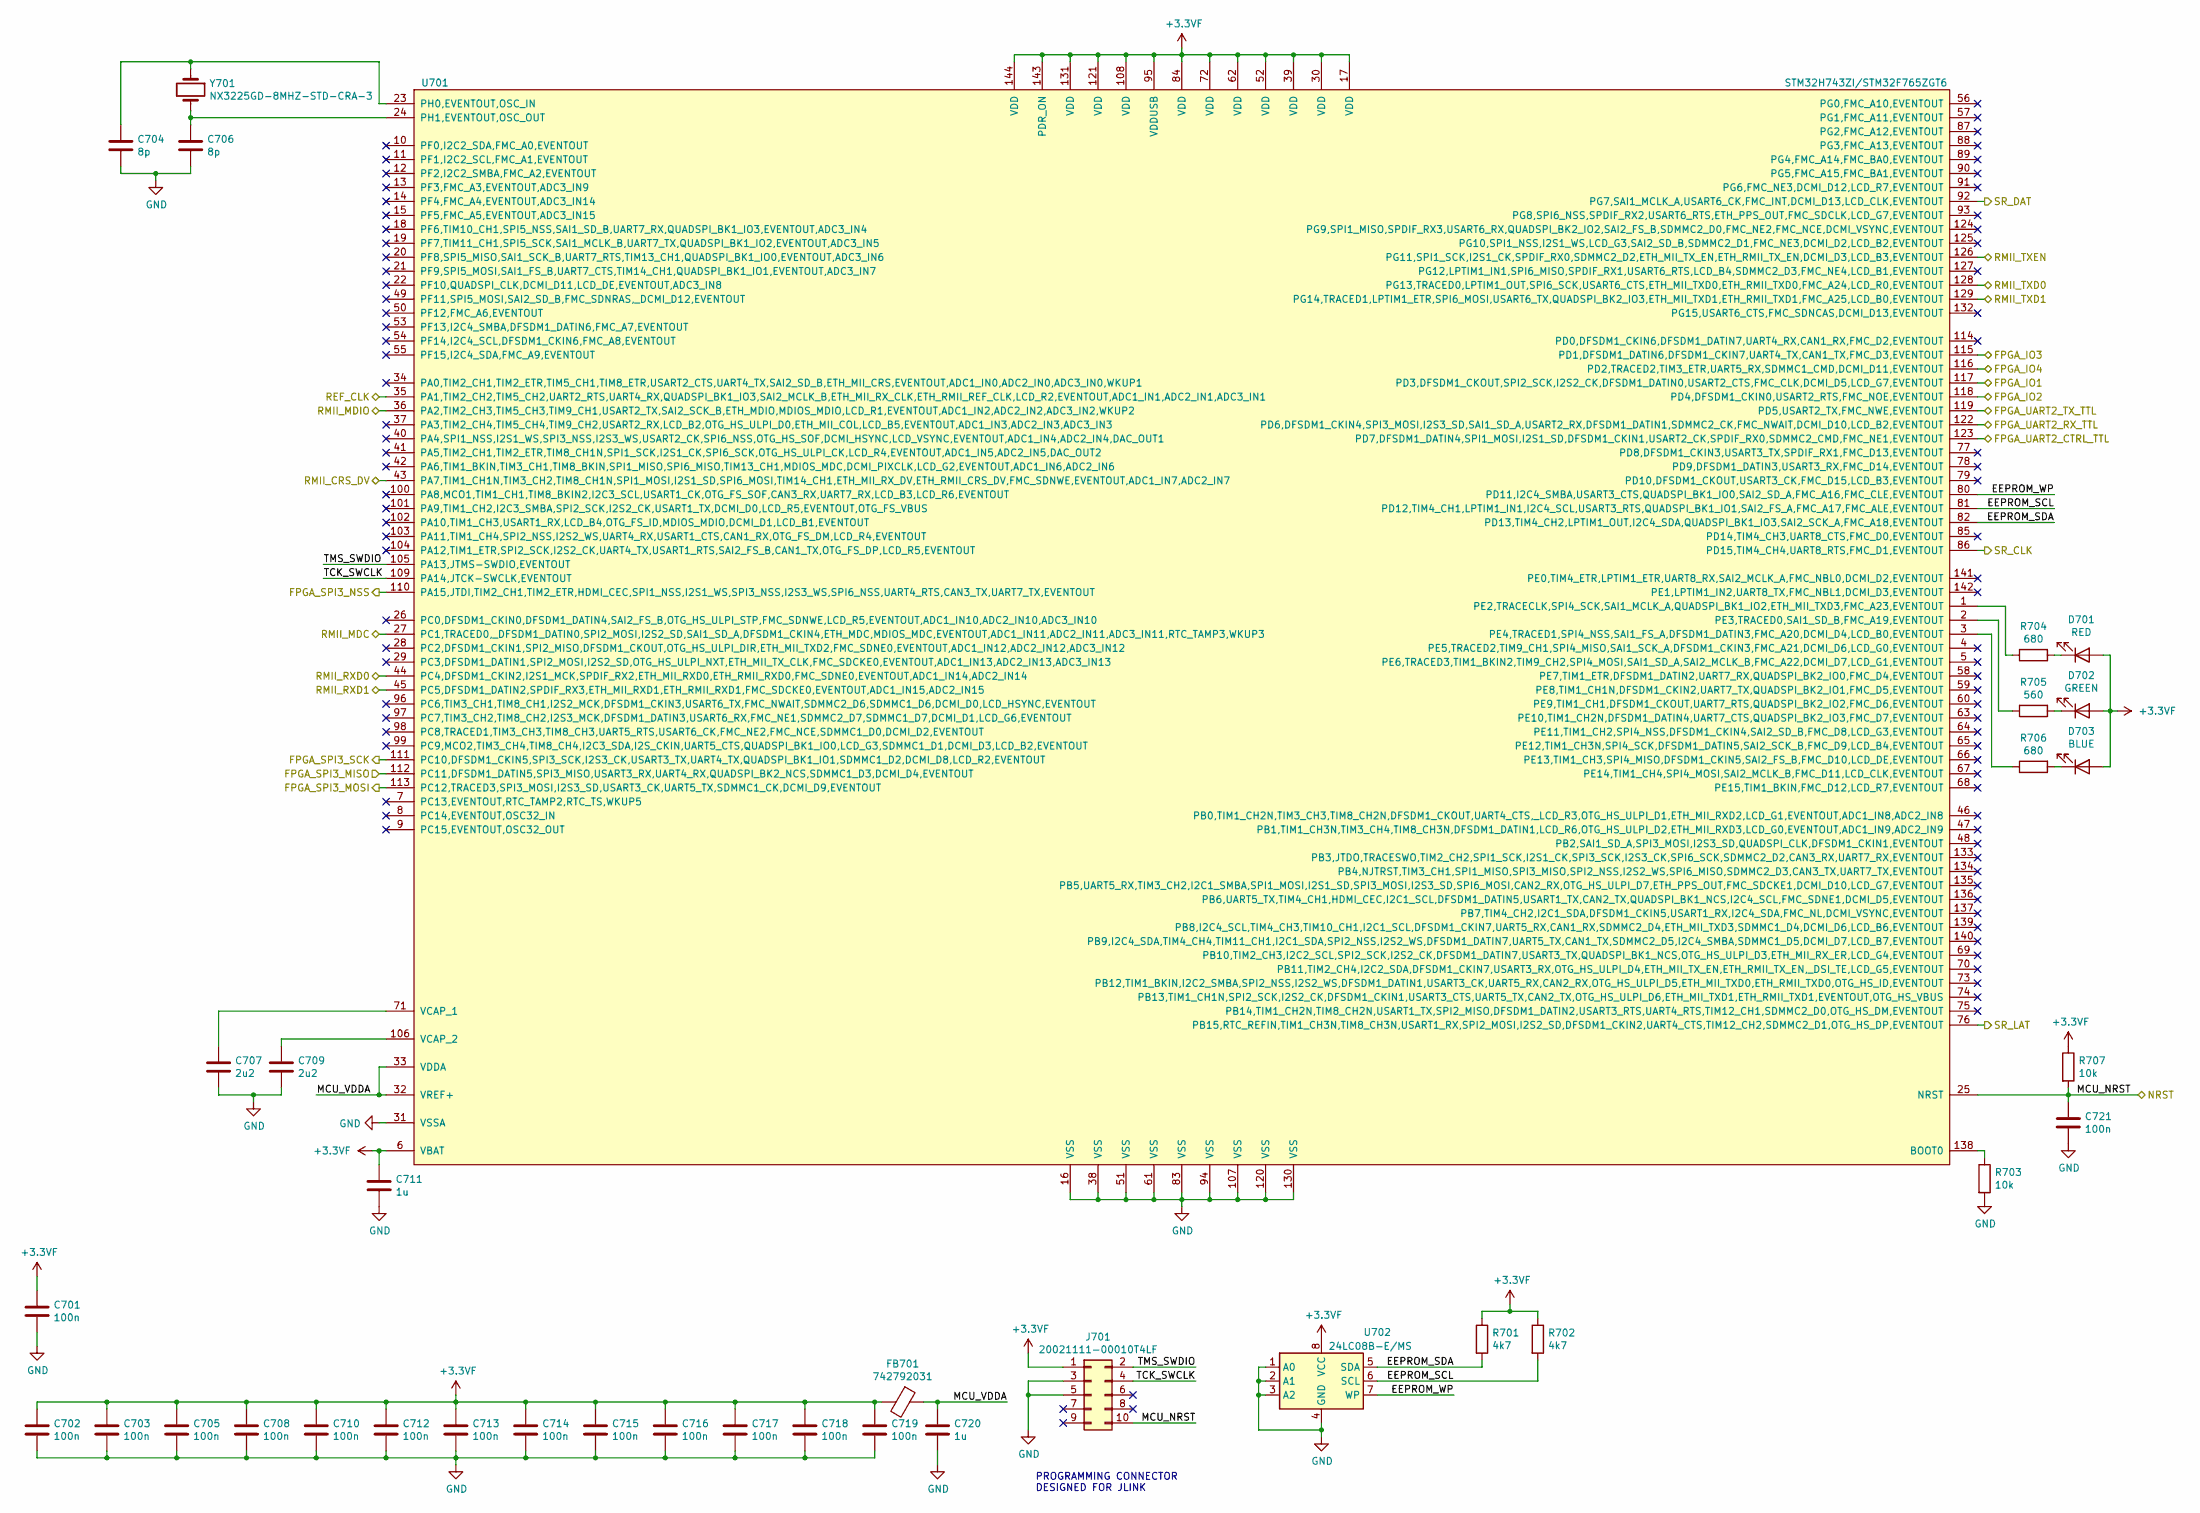
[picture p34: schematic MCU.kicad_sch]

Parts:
C701, C702, C703, C705, C708, C710, C712, C713, C714, C715, C716, C717, C718, C719, C721: 100n; C_0603_1608Metric_Pad1.05x0.95mm_HandSolder
C704, C706: 8p; C_0603_1608Metric_Pad1.05x0.95mm_HandSolder
C707, C709: 2u2; C_0805_2012Metric_Pad1.15x1.40mm_HandSolder
C711, C720: 1u; C_0603_1608Metric_Pad1.05x0.95mm_HandSolder
D701: RED; LED_0603_1608Metric_Pad1.05x0.95mm_HandSolder
D702: GREEN; LED_0603_1608Metric_Pad1.05x0.95mm_HandSolder
D703: BLUE; LED_0603_1608Metric_Pad1.05x0.95mm_HandSolder
FB701: 742792031; L_0805_2012Metric_Pad1.15x1.40mm_HandSolder
J701: 20021111-00010T4LF; PinHeader_2x05_P1.27mm_Vertical
R701, R702: 4k7; R_0603_1608Metric_Pad1.05x0.95mm_HandSolder
R703, R707: 10k; R_0603_1608Metric_Pad1.05x0.95mm_HandSolder
R704, R706: 680; R_0603_1608Metric_Pad1.05x0.95mm_HandSolder
R705: 560; R_0603_1608Metric_Pad1.05x0.95mm_HandSolder
U701: STM32H743ZI/STM32F765ZGT6; TQFP-144_20x20mm_P0.5mm
U702: 24LC08B-E/MS; MSOP-8_3x3mm_P0.65mm
Y701: NX3225GD-8MHZ-STD-CRA-3; NX3225GD

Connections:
+3.3VF: C701.1, C702.1, C703.1, C705.1, C708.1, C710.1, C711.1, C712.1, C713.1, C714.1, C715.1, C716.1, C717.1, C718.1, C719.1, D701.2 (A), D702.2 (A), D703.2 (A), FB701.2, J701.1, R701.1, R702.1, R707.1, U701.6 (VBAT), U701.17 (VDD), U701.30 (VDD), U701.39 (VDD), U701.52 (VDD), U701.62 (VDD), U701.72 (VDD), U701.84 (VDD), U701.95 (VDDUSB), U701.108 (VDD), U701.121 (VDD), U701.131 (VDD), U701.143 (PDR_ON), U701.144 (VDD), U702.8 (VCC); also elsewhere on the board
/Ethernet/NRST: C721.1, J701.10, R707.2, U701.25 (NRST); also elsewhere on the board
/Ethernet/REF_CLK: U701.35 (PA1,TIM2_CH2,TIM5_CH2,UART2_RTS,UART4_R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); also elsewhere on the board
/Ethernet/RMII_CRS_DV: U701.43 (PA7,TIM1_CH1N,TIM3_CH2,TIM8_CH1N,SPI1_M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); also elsewhere on the board
/Ethernet/RMII_MDC: U701.27 (PC1,TRACED0,_DFSDM1_DATIN0,SPI2_MOSI,I2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); also elsewhere on the board
/Ethernet/RMII_MDIO: U701.36 (PA2,TIM2_CH3,TIM5_CH3,TIM9_CH1,USART2_T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); also elsewhere on the board
/Ethernet/RMII_RXD0: U701.44 (PC4,DFSDM1_CKIN2,I2S1_MCK,SPDIF_RX2,ETH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); also elsewhere on the board
/Ethernet/RMII_RXD1: U701.45 (PC5,DFSDM1_DATIN2,SPDIF_RX3,ETH_MII_RXD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); also elsewhere on the board
/Ethernet/RMII_TXD0: U701.128 (PG13,TRACED0,LPTIM1_OUT,SPI6_SCK,USART6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); also elsewhere on the board
/Ethernet/RMII_TXD1: U701.129 (PG14,TRACED1,LPTIM1_ETR,SPI6_MOSI,USART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); also elsewhere on the board
/Ethernet/RMII_TXEN: U701.126 (PG11,SPI1_SCK,I2S1_CK,SPDIF_RX0,SDMMC2_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); also elsewhere on the board
/FPGA/FPGA_IO1: U701.117 (PD3,DFSDM1_CKOUT,SPI2_SCK,I2S2_CK,DFSDM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); also elsewhere on the board
/FPGA/FPGA_IO2: U701.118 (PD4,DFSDM1_CKIN0,USART2_RTS,FMC_NOE,EVE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); also elsewhere on the board
/FPGA/FPGA_IO3: U701.115 (PD1,DFSDM1_DATIN6,DFSDM1_CKIN7,UART4_TX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); also elsewhere on the board
/FPGA/FPGA_IO4: U701.116 (PD2,TRACED2,TIM3_ETR,UART5_RX,SDMMC1_CM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); also elsewhere on the board
/FPGA/FPGA_SPI3_MISO: U701.112 (PC11,DFSDM1_DATIN5,SPI3_MISO,USART3_RX,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); also elsewhere on the board
/FPGA/FPGA_SPI3_MOSI: U701.113 (PC12,TRACED3,SPI3_MOSI,I2S3_SD,USART3_C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); also elsewhere on the board
/FPGA/FPGA_SPI3_NSS: U701.110 (PA15,JTDI,TIM2_CH1,TIM2_ETR,HDMI_CEC,SP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); also elsewhere on the board
/FPGA/FPGA_SPI3_SCK: U701.111 (PC10,DFSDM1_CKIN5,SPI3_SCK,I2S3_CK,USAR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); also elsewhere on the board
/FPGA/FPGA_UART2_CTRL_TTL: U701.123 (PD7,DFSDM1_DATIN4,SPI1_MOSI,I2S1_SD,DFS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); also elsewhere on the board
/FPGA/FPGA_UART2_RX_TTL: U701.122 (PD6,DFSDM1_CKIN4,SPI3_MOSI,I2S3_SD,SAI1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); also elsewhere on the board
/FPGA/FPGA_UART2_TX_TTL: U701.119 (PD5,USART2_TX,FMC_NWE,EVENTOUT); also elsewhere on the board
/Input/SR_CLK: U701.86 (PD15,TIM4_CH4,UART8_RTS,FMC_D1,EVENTOUT); also elsewhere on the board
/Input/SR_DAT: U701.92 (PG7,SAI1_MCLK_A,USART6_CK,FMC_INT,DCMI_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); also elsewhere on the board
/Input/SR_LAT: U701.76 (PB15,RTC_REFIN,TIM1_CH3N,TIM8_CH3N,USAR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); also elsewhere on the board
/MCU/EEPROM_SCL: R702.2, U701.81 (PD12,TIM4_CH1,LPTIM1_IN1,I2C4_SCL,USART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), U702.6 (SCL)
/MCU/EEPROM_SDA: R701.2, U701.82 (PD13,TIM4_CH2,LPTIM1_OUT,I2C4_SDA,QUADS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), U702.5 (SDA)
/MCU/EEPROM_WP: U701.80 (PD11,I2C4_SMBA,USART3_CTS,QUADSPI_BK1_I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), U702.7 (WP)
/MCU/MCU_VDDA: C720.1, FB701.1, U701.32 (VREF+), U701.33 (VDDA)
/MCU/TCK_SWCLK: J701.4, U701.109 (PA14,JTCK-SWCLK,EVENTOUT)
/MCU/TMS_SWDIO: J701.2, U701.105 (PA13,JTMS-SWDIO,EVENTOUT)
AGNDF: C701.2, C702.2, C703.2, C704.2, C705.2, C706.2, C707.2, C708.2, C709.2, C710.2, C711.2, C712.2, C713.2, C714.2, C715.2, C716.2, C717.2, C718.2, C719.2, C720.2, C721.2, J701.3, J701.5, R703.2, U701.16 (VSS), U701.31 (VSSA), U701.38 (VSS), U701.51 (VSS), U701.61 (VSS), U701.83 (VSS), U701.94 (VSS), U701.107 (VSS), U701.120 (VSS), U701.130 (VSS), U702.1 (A0), U702.2 (A1), U702.3 (A2), U702.4 (GND); also elsewhere on the board
unnamed: C704.1, U701.23 (PH0,EVENTOUT,OSC_IN), Y701.1
unnamed: C706.1, U701.24 (PH1,EVENTOUT,OSC_OUT), Y701.2
unnamed: C707.1, U701.71 (VCAP_1)
unnamed: C709.1, U701.106 (VCAP_2)
unnamed: D701.1 (K), R704.2
unnamed: D702.1 (K), R705.2
unnamed: D703.1 (K), R706.2
unnamed: R703.1, U701.138 (BOOT0)
unnamed: R704.1, U701.1 (PE2,TRACECLK,SPI4_SCK,SAI1_MCLK_A,QUADS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)
unnamed: R705.1, U701.2 (PE3,TRACED0,SAI1_SD_B,FMC_A19,EVENTOUT)
unnamed: R706.1, U701.3 (PE4,TRACED1,SPI4_NSS,SAI1_FS_A,DFSDM1_D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)

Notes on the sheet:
PROGRAMMING CONNECTOR DESIGNED FOR JLINK

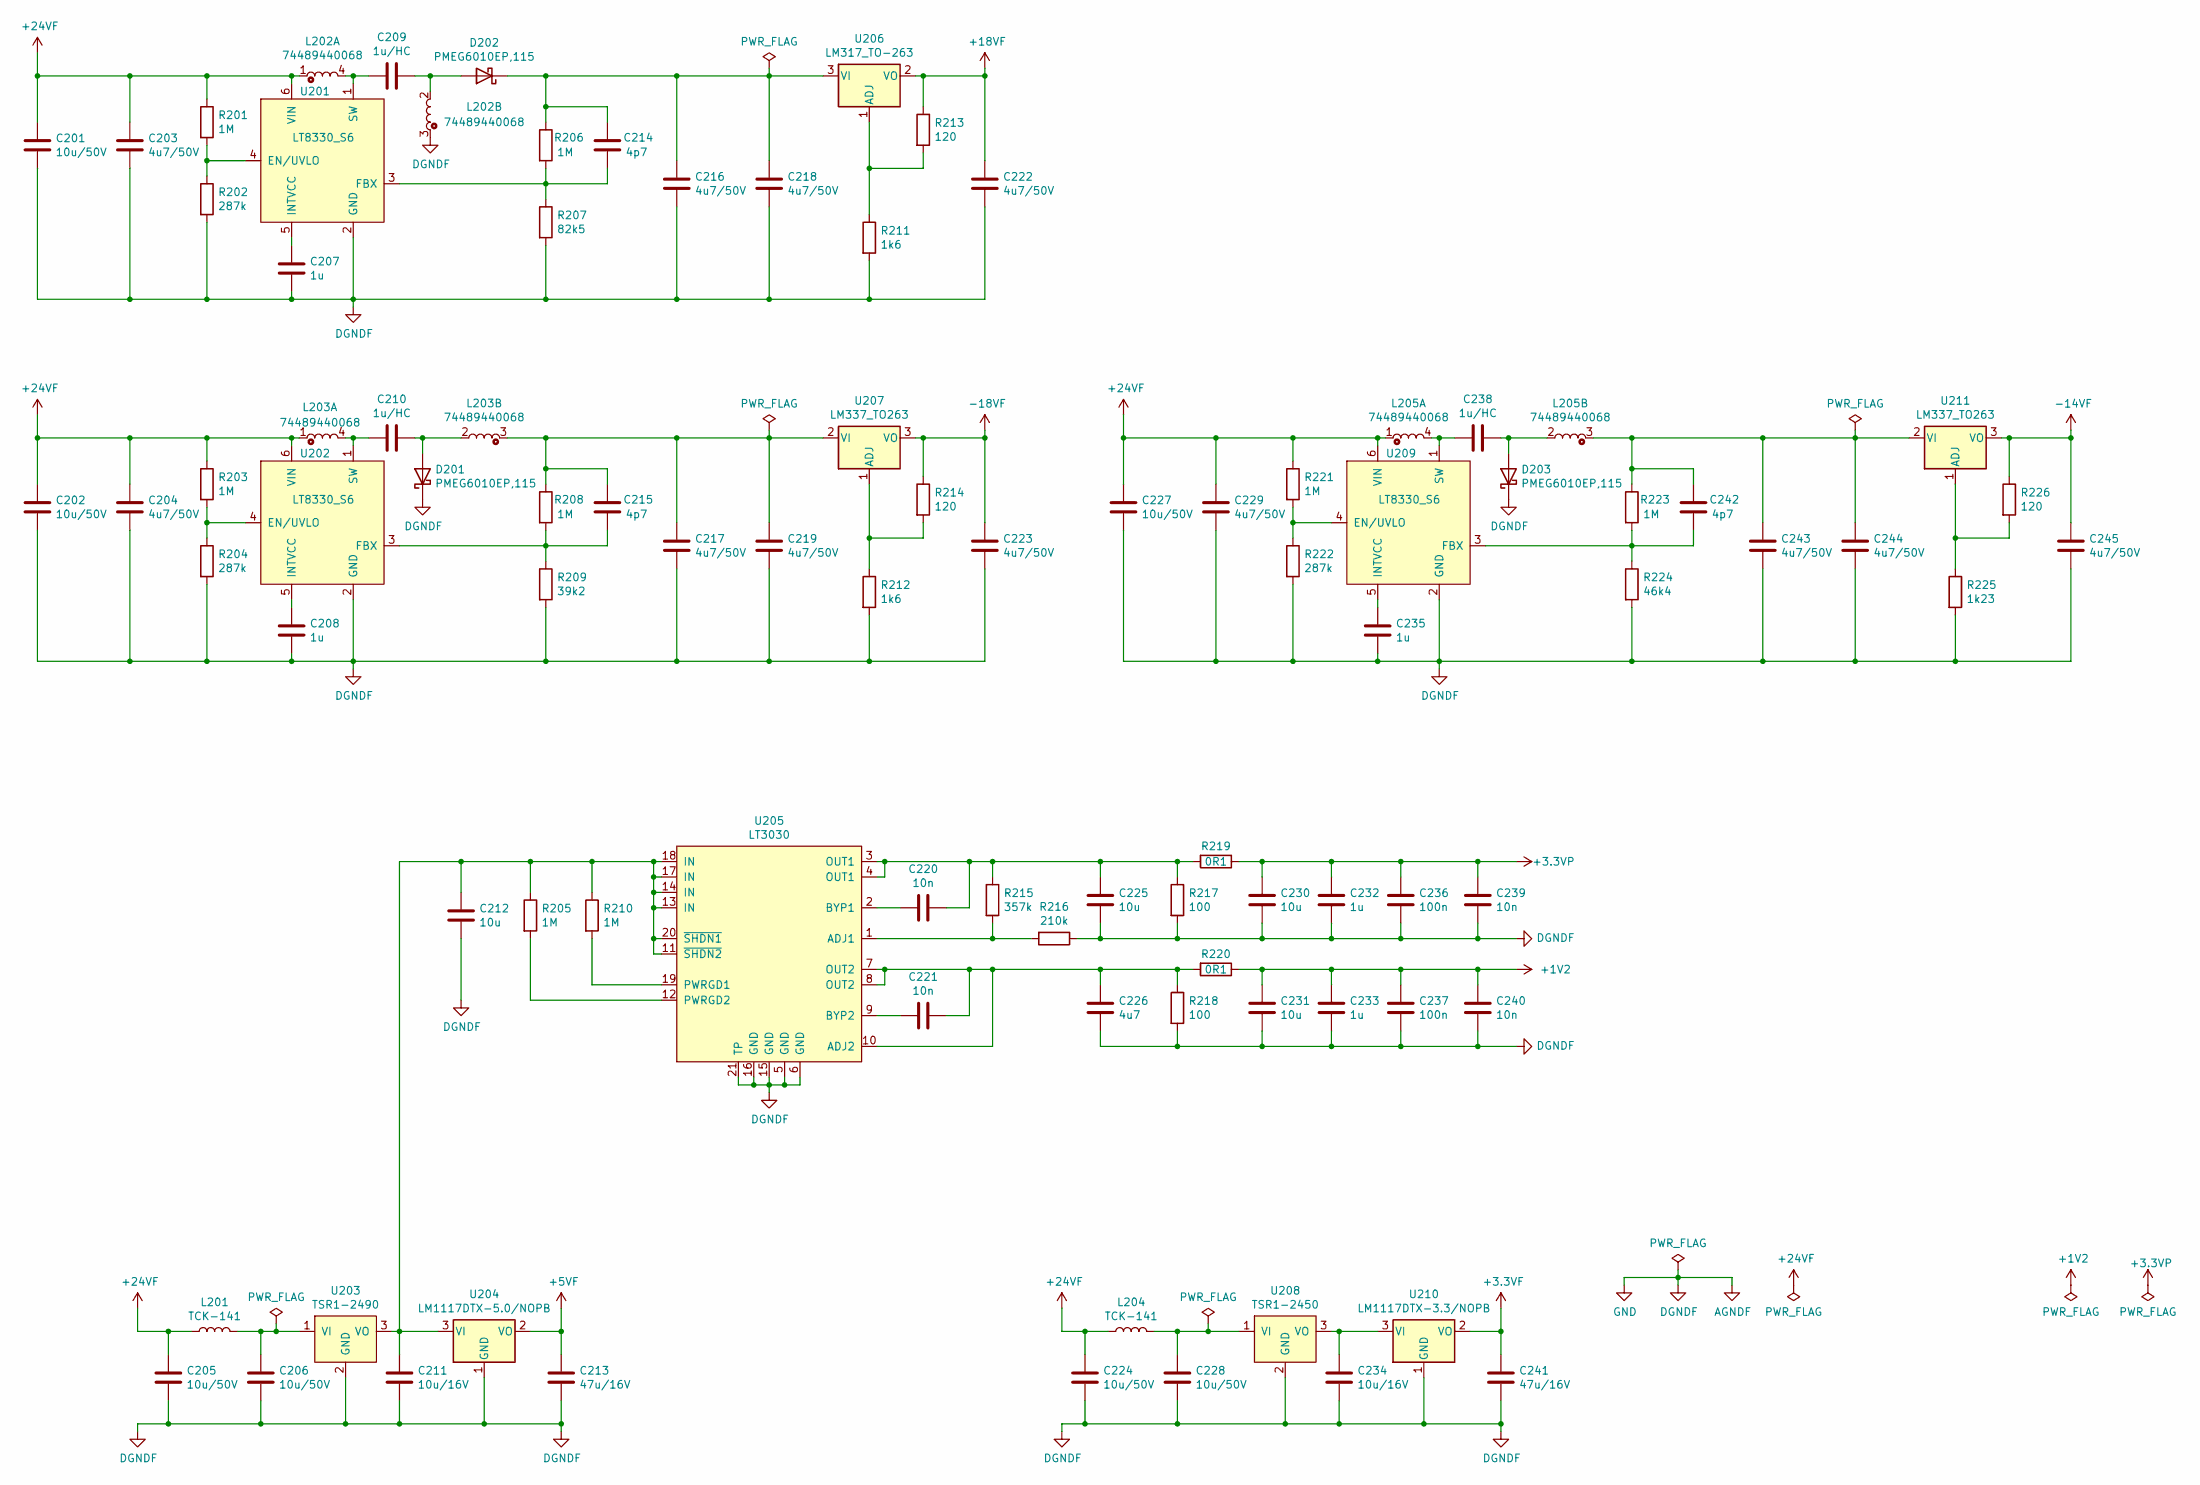
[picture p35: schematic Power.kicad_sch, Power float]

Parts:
C201, C202, C205, C206, C224, C227, C228: 10u/50V; C_1206_3216Metric_Pad1.42x1.75mm_HandSolder
C203, C204, C216, C217, C218, C219, C222, C223, C229, C243, C244, C245: 4u7/50V; C_1206_3216Metric_Pad1.42x1.75mm_HandSolder
C207, C208, C232, C233, C235: 1u; C_0603_1608Metric_Pad1.05x0.95mm_HandSolder
C209, C210, C238: 1u/HC; C_1206_3216Metric_Pad1.42x1.75mm_HandSolder
C211, C234: 10u/16V; C_1206_3216Metric_Pad1.42x1.75mm_HandSolder
C212, C225, C230, C231: 10u; C_0805_2012Metric_Pad1.15x1.40mm_HandSolder
C213, C241: 47u/16V; C_1206_3216Metric_Pad1.42x1.75mm_HandSolder
C214, C215, C242: 4p7; C_0603_1608Metric_Pad1.05x0.95mm_HandSolder
C220, C221, C239, C240: 10n; C_0603_1608Metric_Pad1.05x0.95mm_HandSolder
C226: 4u7; C_0805_2012Metric_Pad1.15x1.40mm_HandSolder
C236, C237: 100n; C_0603_1608Metric_Pad1.05x0.95mm_HandSolder
D201, D202, D203: PMEG6010EP,115; D_SOD-128
L201, L204: TCK-141
L202, L203, L205: 74489440068
R201, R203, R205, R206, R208, R210, R221, R223: 1M; R_0603_1608Metric_Pad1.05x0.95mm_HandSolder
R202, R204, R222: 287k; R_0603_1608Metric_Pad1.05x0.95mm_HandSolder
R207: 82k5; R_0603_1608Metric_Pad1.05x0.95mm_HandSolder
R209: 39k2; R_0603_1608Metric_Pad1.05x0.95mm_HandSolder
R211, R212: 1k6; R_0603_1608Metric_Pad1.05x0.95mm_HandSolder
R213, R214, R226: 120; R_0603_1608Metric_Pad1.05x0.95mm_HandSolder
R215: 357k; R_0603_1608Metric_Pad1.05x0.95mm_HandSolder
R216: 210k; R_0603_1608Metric_Pad1.05x0.95mm_HandSolder
R217, R218: 100; R_0603_1608Metric_Pad1.05x0.95mm_HandSolder
R219, R220: 0R1; R_0805_2012Metric_Pad1.15x1.40mm_HandSolder
R224: 46k4; R_0603_1608Metric_Pad1.05x0.95mm_HandSolder
R225: 1k23; R_0603_1608Metric_Pad1.05x0.95mm_HandSolder
U201, U202, U209: LT8330_S6; TSOT-23-6_HandSoldering
U203: TSR1-2490; TSR1
U204: LM1117DTX-5.0/NOPB; TO-252-2
U205: LT3030; ETSSOP-20-1EP_4.4x6.5mm_P0.65mm_EP3x4.2mm
U206: LM317_TO-263; TO-263-2
U207, U211: LM337_TO263; TO-263-2
U208: TSR1-2450; TSR1
U210: LM1117DTX-3.3/NOPB; TO-252-2

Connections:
+1V2: C231.1, C233.1, C237.1, C240.1, R220.1; also elsewhere on the board
+3.3VF: C241.1, U210.2 (VO); also elsewhere on the board
+3.3VP: C230.1, C232.1, C236.1, C239.1, R219.1; also elsewhere on the board
+5VF: C213.1, U204.2 (VO); also elsewhere on the board
+18VF: C222.1, R213.1, U206.2 (VO); also elsewhere on the board
+24VF: C201.1, C202.1, C203.1, C204.1, C205.1, C224.1, C227.1, C229.1, L201.1, L202.1, L203.1, L204.1, L205.1, R201.1, R203.1, R221.1, U201.6 (VIN), U202.6 (VIN), U209.6 (VIN); also elsewhere on the board
-14VF: C245.1, R226.1, U211.3 (VO); also elsewhere on the board
-18VF: C223.1, R214.1, U207.3 (VO); also elsewhere on the board
AGNDF: C201.2, C202.2, C203.2, C204.2, C205.2, C206.2, C207.2, C208.2, C211.2, C212.2, C213.2, C216.2, C217.2, C218.2, C219.2, C222.2, C223.2, C224.2, C225.2, C226.2, C227.2, C228.2, C229.2, C230.2, C231.2, C232.2, C233.2, C234.2, C235.2, C236.2, C237.2, C239.2, C240.2, C241.2, C243.2, C244.2, C245.2, D201.1 (K), D203.1 (K), L202.3, R202.2, R204.2, R207.2, R209.2, R211.2, R212.2, R216.1, R217.2, R218.2, R222.2, R224.2, R225.2, U201.2 (GND), U202.2 (GND), U203.2 (GND), U204.1 (GND), U205.5 (GND), U205.6 (GND), U205.15 (GND), U205.16 (GND), U205.21 (TP), U208.2 (GND), U209.2 (GND), U210.1 (GND); also elsewhere on the board
unnamed: C206.1, L201.2, U203.1 (VI)
unnamed: C207.1, U201.5 (INTVCC)
unnamed: C208.1, U202.5 (INTVCC)
unnamed: C209.1, D202.2 (A), L202.2
unnamed: C209.2, L202.4, U201.1 (SW)
unnamed: C210.1, D201.2 (A), L203.2
unnamed: C210.2, L203.4, U202.1 (SW)
unnamed: C211.1, C212.1, R205.1, R210.1, U203.3 (VO), U204.3 (VI), U205.11 (~SHDN2), U205.13 (IN), U205.14 (IN), U205.17 (IN), U205.18 (IN), U205.20 (~SHDN1)
unnamed: C214.1, C216.1, C218.1, D202.1 (K), R206.1, U206.3 (VI)
unnamed: C214.2, R206.2, R207.1, U201.3 (FBX)
unnamed: C215.1, C217.1, C219.1, L203.3, R208.1, U207.2 (VI)
unnamed: C215.2, R208.2, R209.1, U202.3 (FBX)
unnamed: C220.1, C225.1, R215.1, R217.1, R219.2, U205.3 (OUT1), U205.4 (OUT1)
unnamed: C220.2, U205.2 (BYP1)
unnamed: C221.1, C226.1, R218.1, R220.2, U205.7 (OUT2), U205.8 (OUT2), U205.10 (ADJ2)
unnamed: C221.2, U205.9 (BYP2)
unnamed: C228.1, L204.2, U208.1 (VI)
unnamed: C234.1, U208.3 (VO), U210.3 (VI)
unnamed: C235.1, U209.5 (INTVCC)
unnamed: C238.1, D203.2 (A), L205.2
unnamed: C238.2, L205.4, U209.1 (SW)
unnamed: C242.1, C243.1, C244.1, L205.3, R223.1, U211.2 (VI)
unnamed: C242.2, R223.2, R224.1, U209.3 (FBX)
unnamed: R201.2, R202.1, U201.4 (EN/UVLO)
unnamed: R203.2, R204.1, U202.4 (EN/UVLO)
unnamed: R205.2, U205.12 (PWRGD2)
unnamed: R210.2, U205.19 (PWRGD1)
unnamed: R211.1, R213.2, U206.1 (ADJ)
unnamed: R212.1, R214.2, U207.1 (ADJ)
unnamed: R215.2, R216.2, U205.1 (ADJ1)
unnamed: R221.2, R222.1, U209.4 (EN/UVLO)
unnamed: R225.1, R226.2, U211.1 (ADJ)

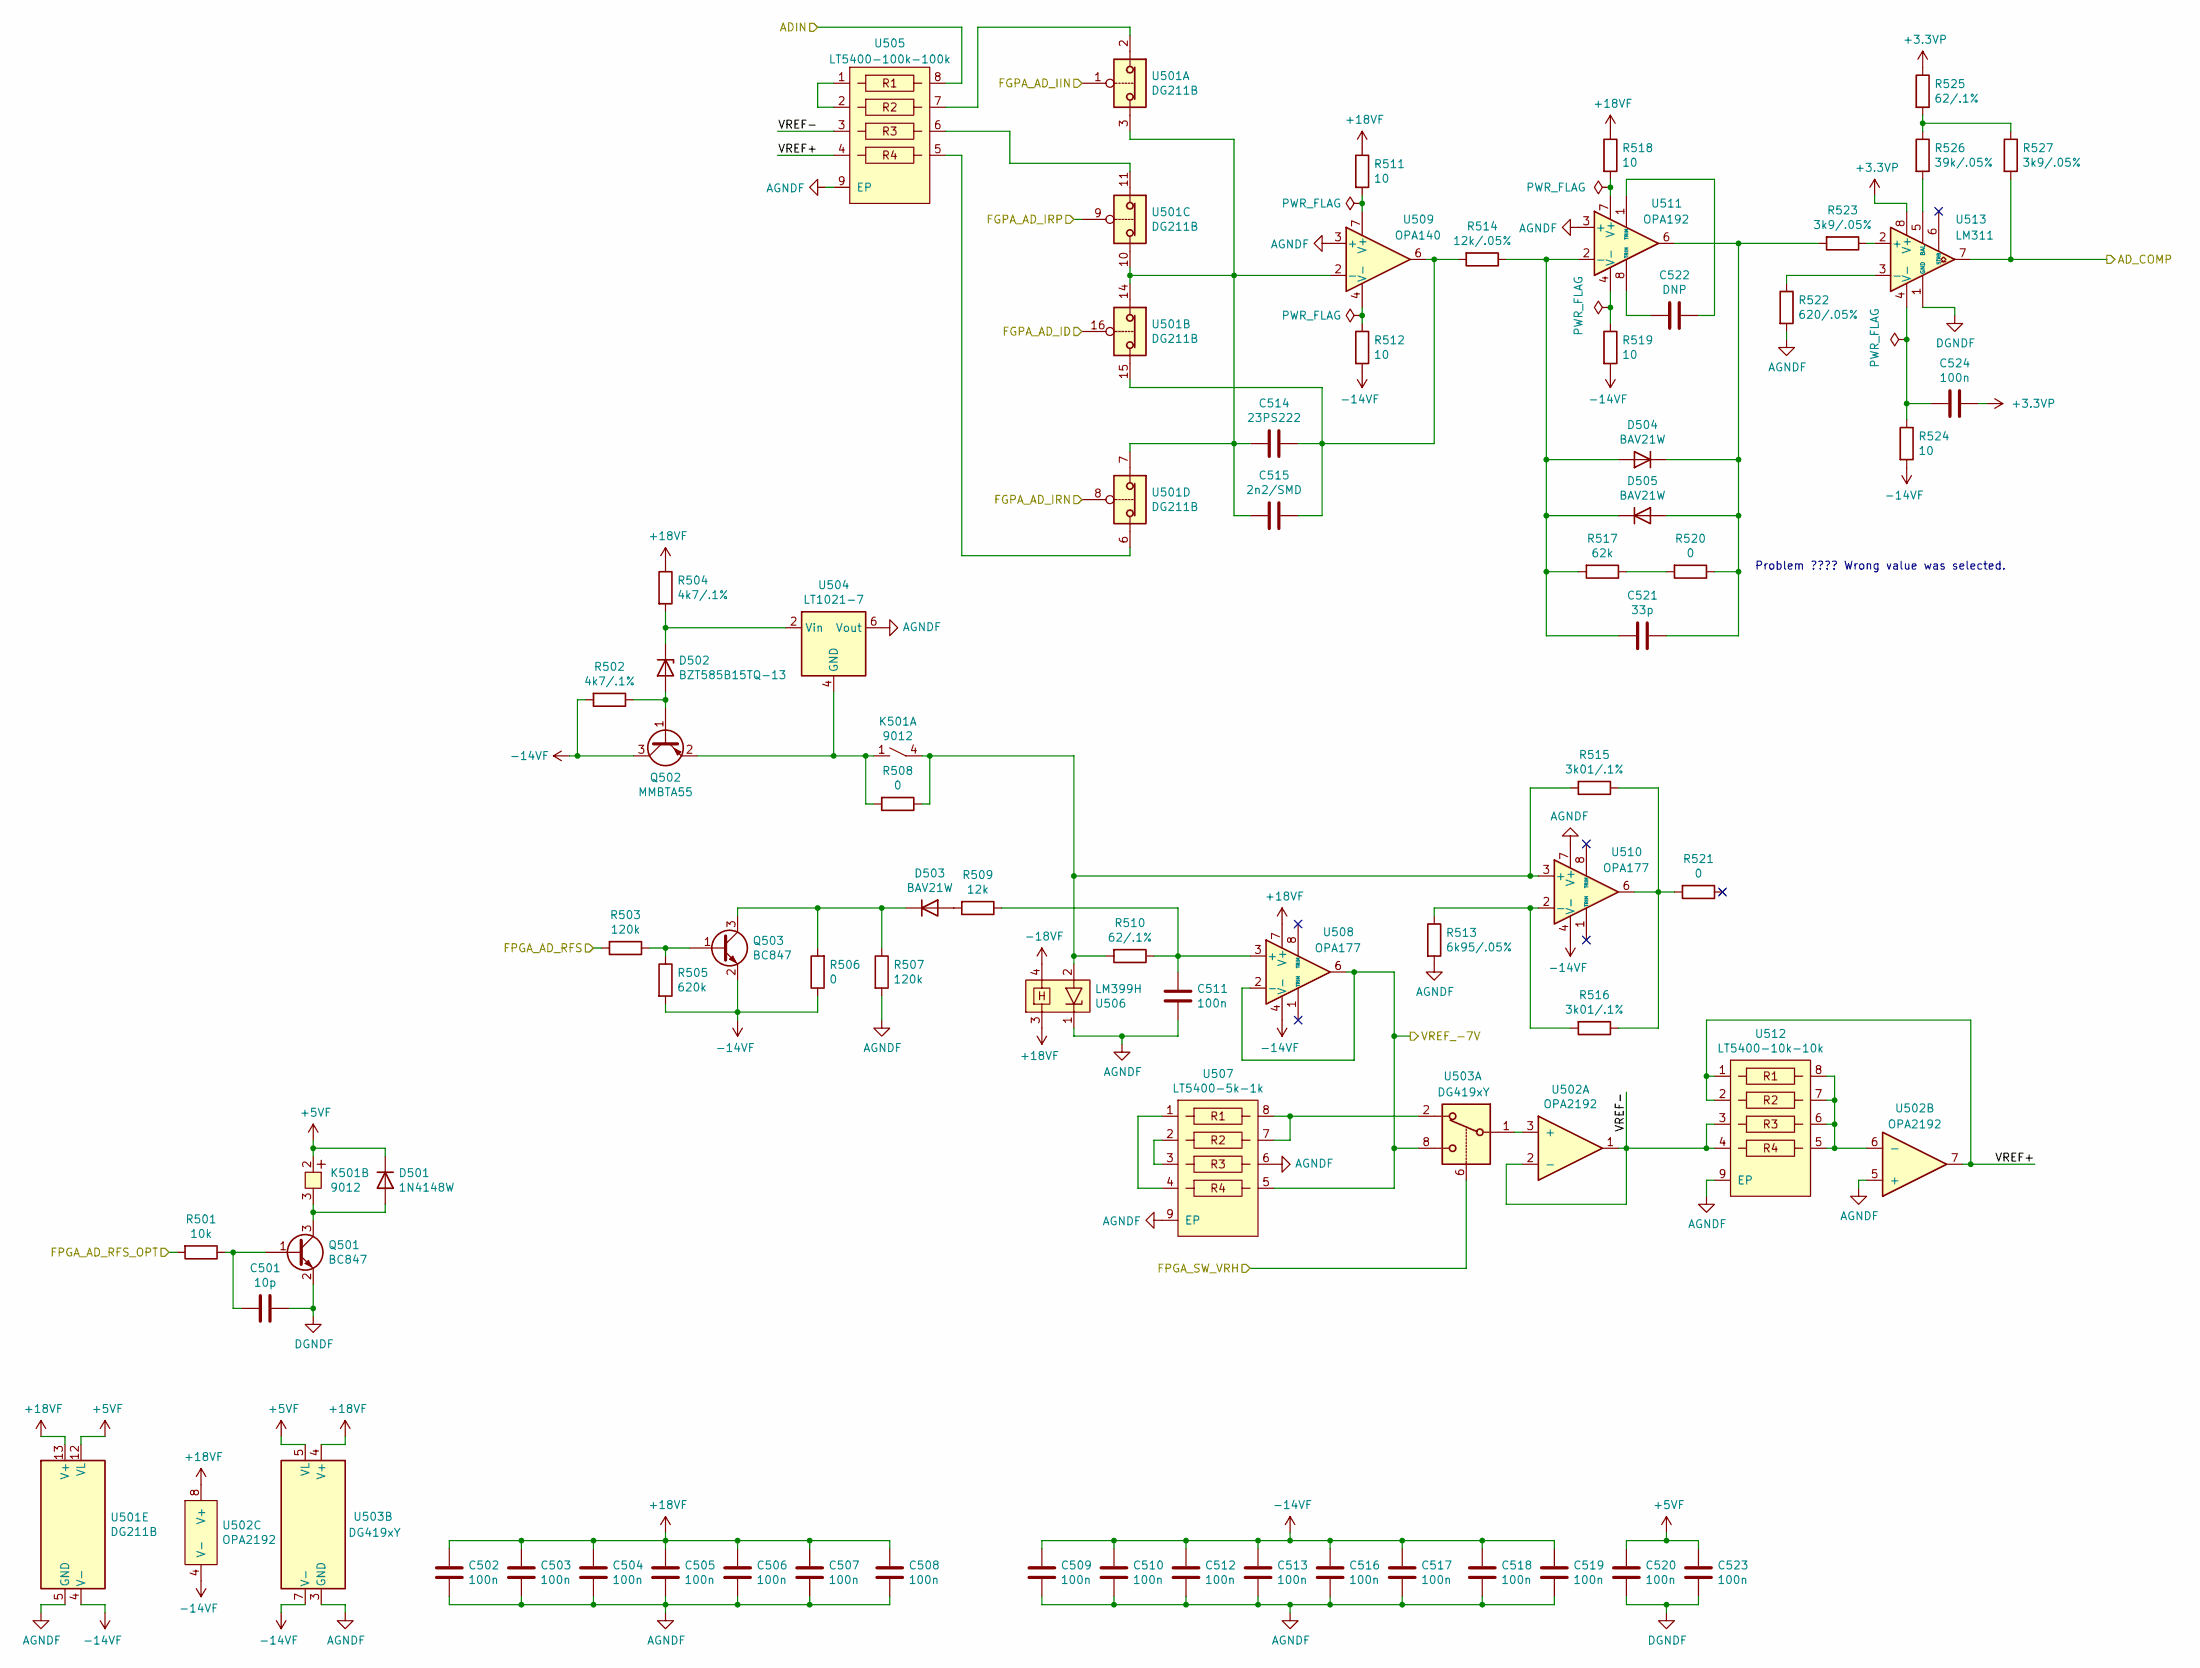
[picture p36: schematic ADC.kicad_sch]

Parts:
C501: 10p; C_0603_1608Metric_Pad1.05x0.95mm_HandSolder
C502, C503, C504, C505, C506, C507, C508, C509, C510, C511, C512, C513, C516, C517, C518, C519, C520, C523, C524: 100n; C_0603_1608Metric_Pad1.05x0.95mm_HandSolder
C514: 23PS222; C_Axial_L12.0mm_D6.5mm_P15.00mm_Horizontal
C515: 2n2/SMD; C_0603_1608Metric_Pad1.05x0.95mm_HandSolder
C521: 33p; C_0603_1608Metric_Pad1.05x0.95mm_HandSolder
C522: DNP; C_0603_1608Metric_Pad1.05x0.95mm_HandSolder
D501: 1N4148W; D_SOD-123
D502: BZT585B15TQ-13; D_SOD-523
D503, D504, D505: BAV21W; D_SOD-123
K501: 9012
Q501, Q503: BC847; SOT-23
Q502: MMBTA55; SOT-23
R501: 10k; R_0603_1608Metric_Pad1.05x0.95mm_HandSolder
R502, R504: 4k7/.1%; R_0603_1608Metric_Pad1.05x0.95mm_HandSolder
R503, R507: 120k; R_0603_1608Metric_Pad1.05x0.95mm_HandSolder
R505: 620k; R_0603_1608Metric_Pad1.05x0.95mm_HandSolder
R506, R508, R520, R521: 0; R_0603_1608Metric_Pad1.05x0.95mm_HandSolder
R509: 12k; R_0603_1608Metric_Pad1.05x0.95mm_HandSolder
R510, R525: 62/.1%; R_0603_1608Metric_Pad1.05x0.95mm_HandSolder
R511, R512, R518, R519, R524: 10; R_0603_1608Metric_Pad1.05x0.95mm_HandSolder
R513: 6k95/.05%; R_1206_3216Metric_Pad1.42x1.75mm_HandSolder
R514: 12k/.05%; R_0603_1608Metric_Pad1.05x0.95mm_HandSolder
R515, R516: 3k01/.1%; R_0603_1608Metric_Pad1.05x0.95mm_HandSolder
R517: 62k; R_0603_1608Metric_Pad1.05x0.95mm_HandSolder
R522: 620/.05%; R_0603_1608Metric_Pad1.05x0.95mm_HandSolder
R523, R527: 3k9/.05%; R_0603_1608Metric_Pad1.05x0.95mm_HandSolder
R526: 39k/.05%; R_0603_1608Metric_Pad1.05x0.95mm_HandSolder
U501: DG211B; SOIC-16_3.9x9.9mm_P1.27mm
U502: OPA2192; SOIC-8_3.9x4.9mm_P1.27mm
U503: DG419xY; SOIC-8_3.9x4.9mm_P1.27mm
U504: LT1021-7; SOIC-8_3.9x4.9mm_P1.27mm
U505: LT5400-100k-100k; MSOP-8-1EP_3x3mm_P0.65mm_EP1.73x1.85mm_ThermalVias
U506: LM399H; LMx99
U507: LT5400-5k-1k; MSOP-8-1EP_3x3mm_P0.65mm_EP1.73x1.85mm_ThermalVias
U508, U510: OPA177; SOIC-8_3.9x4.9mm_P1.27mm
U509: OPA140; SOIC-8_3.9x4.9mm_P1.27mm
U511: OPA192; SOIC-8_3.9x4.9mm_P1.27mm
U512: LT5400-10k-10k; MSOP-8-1EP_3x3mm_P0.65mm_EP1.73x1.85mm_ThermalVias
U513: LM311; SOIC-8_3.9x4.9mm_P1.27mm

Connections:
+3.3VP: C524.1, R525.1, U513.8 (V+); also elsewhere on the board
+5VF: C520.1, C523.1, D501.1 (K), K501.2, U501.12 (VL), U503.5 (VL); also elsewhere on the board
+18VF: C502.1, C503.1, C504.1, C505.1, C506.1, C507.1, C508.1, R504.1, R511.1, R518.1, U501.13 (V+), U502.8 (V+), U503.4 (V+), U506.3, U508.7 (V+); also elsewhere on the board
-14VF: C509.1, C510.1, C512.1, C513.1, C516.1, C517.1, C518.1, C519.1, Q502.3 (C), Q503.2 (E), R502.2, R505.2, R506.1, R512.2, R519.2, R524.2, U501.4 (V-), U502.4 (V-), U503.7 (V-), U508.4 (V-), U510.4 (V-); also elsewhere on the board
-18VF: U506.4; also elsewhere on the board
/ADC/ADIN: U505.8; also elsewhere on the board
/ADC/FGPA_AD_ID: U501.16; also elsewhere on the board
/ADC/FGPA_AD_IIN: U501.1; also elsewhere on the board
/ADC/FGPA_AD_IRN: U501.8; also elsewhere on the board
/ADC/FGPA_AD_IRP: U501.9; also elsewhere on the board
/ADC/FPGA_AD_RFS: R503.2; also elsewhere on the board
/ADC/FPGA_AD_RFS_OPT: R501.2; also elsewhere on the board
/ADC/VREF+: U502.7, U505.4, U512.1, U512.2
/ADC/VREF-: U502.1, U502.2 (-), U505.3, U512.3, U512.4
/ADC/VREF_-7V: U503.8, U507.5, U508.2 (-), U508.6; also elsewhere on the board
/FPGA/ADC_COMP: R527.2, U513.7; also elsewhere on the board
/FPGA/FGPA_AD_VRH: U503.6; also elsewhere on the board
AGNDF: C501.1, C502.2, C503.2, C504.2, C505.2, C506.2, C507.2, C508.2, C509.2, C510.2, C511.2, C512.2, C513.2, C516.2, C517.2, C518.2, C519.2, C520.2, C523.2, Q501.2 (E), R507.2, R513.2, R522.2, U501.5 (GND), U502.5 (+), U503.3 (GND), U504.6 (Vout), U505.9 (EP), U506.1, U507.6, U507.9 (EP), U509.3 (+), U510.7 (V+), U511.3 (+), U512.9 (EP), U513.1 (GND); also elsewhere on the board
unnamed: C501.2, Q501.1 (B), R501.1
unnamed: C511.1, R509.1, R510.1, U508.3 (+)
unnamed: C514.1, C515.1, R514.2, U501.15, U509.6
unnamed: C514.2, C515.2, U501.3, U501.7, U501.10, U501.14, U509.2 (-)
unnamed: C521.1, D504.1 (K), D505.2 (A), R520.1, R523.2, U511.6
unnamed: C521.2, D504.2 (A), D505.1 (K), R514.1, R517.2, U511.2 (-)
unnamed: C522.1, U511.1 (TRIM)
unnamed: C522.2, U511.8 (TRIM)
unnamed: C524.2, R524.1, U513.4 (V-)
unnamed: D501.2 (A), K501.3, Q501.3 (C)
unnamed: D502.1 (K), R504.2, U504.2 (Vin)
unnamed: D502.2 (A), Q502.1 (B), R502.1
unnamed: D503.1 (K), Q503.3 (C), R506.2, R507.1
unnamed: D503.2 (A), R509.2
unnamed: K501.1, Q502.2 (E), R508.2, U504.4 (GND)
unnamed: K501.4, R508.1, R510.2, R515.2, U506.2, U510.3 (+)
unnamed: Q503.1 (B), R503.1, R505.1
unnamed: R511.2, U509.7 (V+)
unnamed: R512.1, U509.4 (V-)
unnamed: R513.1, R516.2, U510.2 (-)
unnamed: R515.1, R516.1, R521.2, U510.6
unnamed: R517.1, R520.2
unnamed: R518.2, U511.7 (V+)
unnamed: R519.1, U511.4 (V-)
unnamed: R522.1, U513.3 (-)
unnamed: R523.1, U513.2 (+)
unnamed: R525.2, R526.1, R527.1
unnamed: R526.2, U513.5 (BAL)
unnamed: U501.2, U505.7
unnamed: U501.6, U505.5
unnamed: U501.11, U505.6
unnamed: U502.3 (+), U503.1
unnamed: U502.6 (-), U512.5, U512.6, U512.7, U512.8
unnamed: U503.2, U507.7, U507.8
unnamed: U505.1, U505.2
unnamed: U507.1, U507.4
unnamed: U507.2, U507.3

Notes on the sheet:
Problem ???? Wrong value was selected.

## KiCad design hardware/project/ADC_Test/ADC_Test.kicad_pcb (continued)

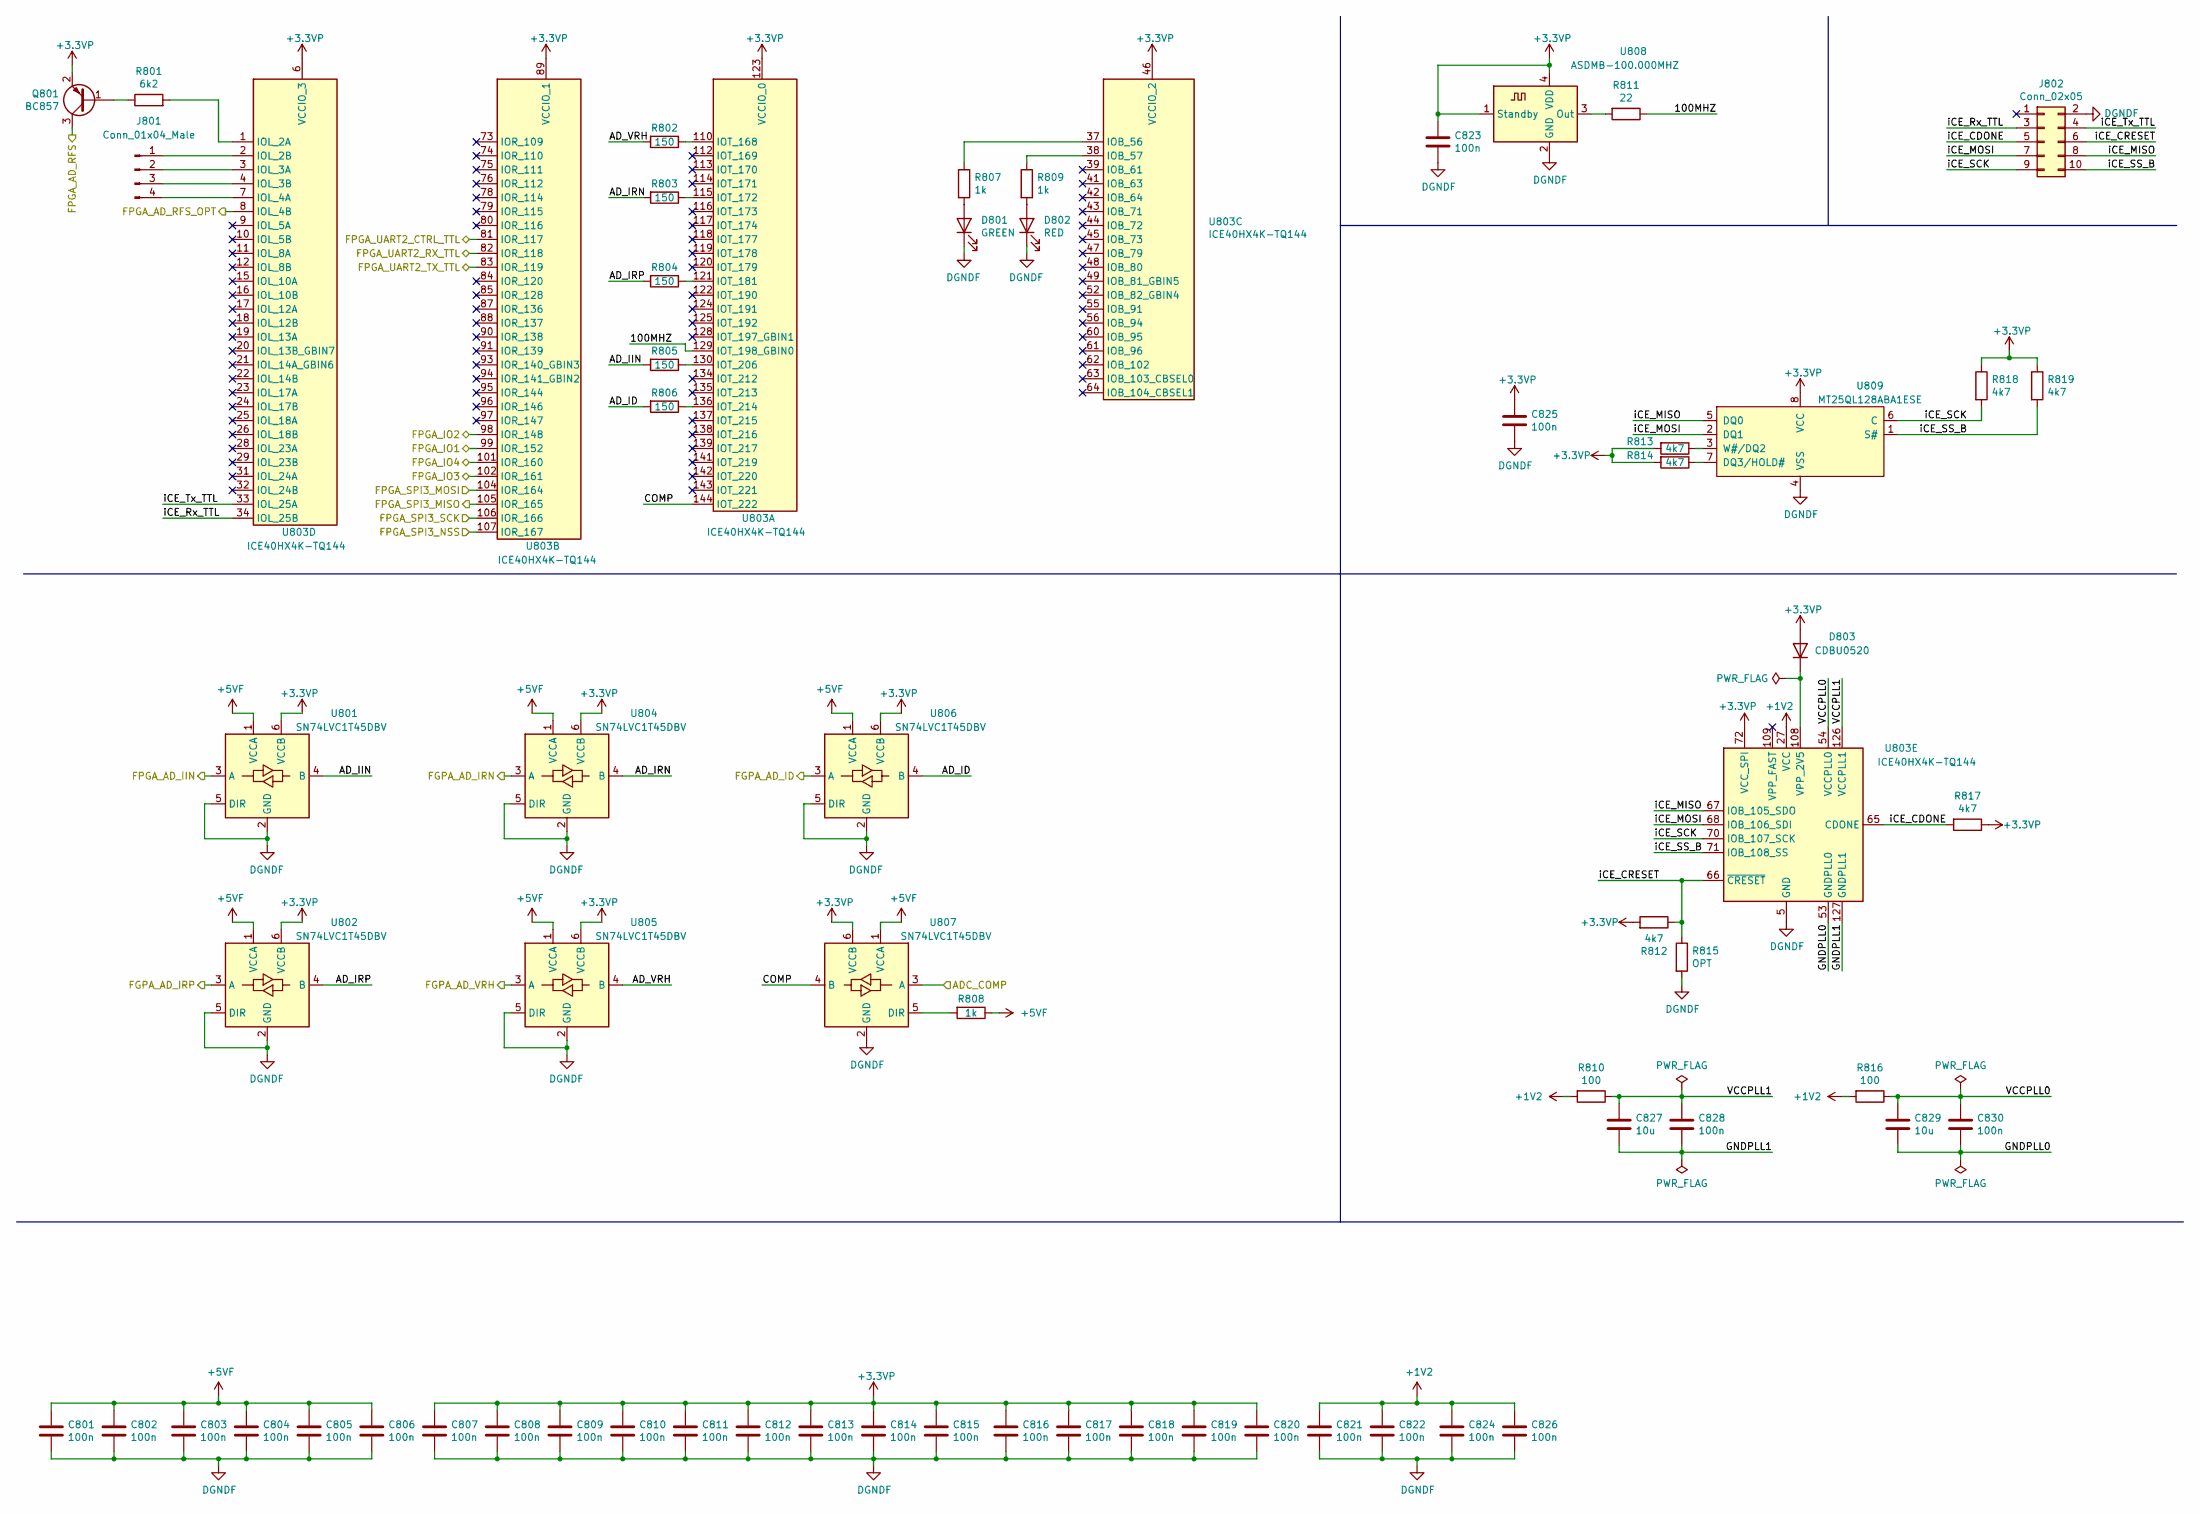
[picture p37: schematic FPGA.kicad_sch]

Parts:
C801, C802, C803, C804, C805, C806, C807, C808, C809, C810, C811, C812, C813, C814, C815, C816, C817, C818, C819, C820, C821, C822, C823, C824, C825, C826, C828, C830: 100n; C_0603_1608Metric_Pad1.05x0.95mm_HandSolder
C827, C829: 10u; C_0805_2012Metric_Pad1.15x1.40mm_HandSolder
D801: GREEN; LED_0603_1608Metric_Pad1.05x0.95mm_HandSolder
D802: RED; LED_0603_1608Metric_Pad1.05x0.95mm_HandSolder
D803: CDBU0520; D_SOD-523
J801: Conn_01x04_Male; PinHeader_1x04_P2.54mm_Vertical
J802: Conn_02x05; PinHeader_2x05_P2.54mm_Vertical
Q801: BC857; SOT-23
R801: 6k2; R_0603_1608Metric_Pad1.05x0.95mm_HandSolder
R802, R803, R804, R805, R806: 150; R_0603_1608Metric_Pad1.05x0.95mm_HandSolder
R807, R808, R809: 1k; R_0603_1608Metric_Pad1.05x0.95mm_HandSolder
R810, R816: 100; R_0603_1608Metric_Pad1.05x0.95mm_HandSolder
R811: 22; R_0603_1608Metric_Pad1.05x0.95mm_HandSolder
R812, R813, R814, R817, R818, R819: 4k7; R_0603_1608Metric_Pad1.05x0.95mm_HandSolder
R815: OPT; R_0603_1608Metric_Pad1.05x0.95mm_HandSolder
U801, U802, U804, U805, U806, U807: SN74LVC1T45DBV; SOT-23-6
U803: ICE40HX4K-TQ144; TQFP-144_20x20mm_P0.5mm
U808: ASDMB-100.000MHZ; Oscillator_SMD_Abracon_ASDMB-4Pin_2.5x2.0mm
U809: MT25QL128ABA1ESE; SOIC-8_5.23x5.23mm_P1.27mm

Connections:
+1V2: C821.1, C822.1, C824.1, C826.1, R810.2, R816.2, U803.27 (VCC), U803.40 (VCC), U803.92 (VCC), U803.111 (VCC); also elsewhere on the board
+3.3VP: C807.1, C808.1, C809.1, C810.1, C811.1, C812.1, C813.1, C814.1, C815.1, C816.1, C817.1, C818.1, C819.1, C820.1, C823.1, C825.1, D803.2 (A), Q801.2 (E), R812.2, R813.2, R814.2, R817.1, R818.1, R819.1, U801.6 (VCCB), U802.6 (VCCB), U803.6 (VCCIO_3), U803.30 (VCCIO_3), U803.46 (VCCIO_2), U803.57 (VCCIO_2), U803.72 (VCC_SPI), U803.89 (VCCIO_1), U803.100 (VCCIO_1), U803.123 (VCCIO_0), U803.131 (VCCIO_0), U804.6 (VCCB), U805.6 (VCCB), U806.6 (VCCB), U807.6 (VCCB), U808.1 (Standby), U808.4 (VDD), U809.8 (VCC); also elsewhere on the board
+5VF: C801.1, C802.1, C803.1, C804.1, C805.1, C806.1, R808.1, U801.1 (VCCA), U802.1 (VCCA), U804.1 (VCCA), U805.1 (VCCA), U806.1 (VCCA), U807.1 (VCCA); also elsewhere on the board
/ADC/FGPA_AD_ID: U806.3 (A); also elsewhere on the board
/ADC/FGPA_AD_IIN: U801.3 (A); also elsewhere on the board
/ADC/FGPA_AD_IRN: U804.3 (A); also elsewhere on the board
/ADC/FGPA_AD_IRP: U802.3 (A); also elsewhere on the board
/ADC/FPGA_AD_RFS: Q801.3 (C); also elsewhere on the board
/ADC/FPGA_AD_RFS_OPT: U803.8 (IOL_4B); also elsewhere on the board
/FPGA/100MHZ: R811.1, U803.129 (IOT_198_GBIN0)
/FPGA/ADC_COMP: U807.3 (A); also elsewhere on the board
/FPGA/AD_ID: R806.2, U806.4 (B)
/FPGA/AD_IIN: R805.2, U801.4 (B)
/FPGA/AD_IRN: R803.2, U804.4 (B)
/FPGA/AD_IRP: R804.2, U802.4 (B)
/FPGA/AD_VRH: R802.2, U805.4 (B)
/FPGA/COMP: U803.144 (IOT_222), U807.4 (B)
/FPGA/FGPA_AD_VRH: U805.3 (A); also elsewhere on the board
/FPGA/FPGA_IO1: U803.99 (IOR_152); also elsewhere on the board
/FPGA/FPGA_IO2: U803.98 (IOR_148); also elsewhere on the board
/FPGA/FPGA_IO3: U803.102 (IOR_161); also elsewhere on the board
/FPGA/FPGA_IO4: U803.101 (IOR_160); also elsewhere on the board
/FPGA/FPGA_SPI3_MISO: U803.105 (IOR_165); also elsewhere on the board
/FPGA/FPGA_SPI3_MOSI: U803.104 (IOR_164); also elsewhere on the board
/FPGA/FPGA_SPI3_NSS: U803.107 (IOR_167); also elsewhere on the board
/FPGA/FPGA_SPI3_SCK: U803.106 (IOR_166); also elsewhere on the board
/FPGA/FPGA_UART2_CTRL_TTL: U803.81 (IOR_117); also elsewhere on the board
/FPGA/FPGA_UART2_RX_TTL: U803.82 (IOR_118); also elsewhere on the board
/FPGA/FPGA_UART2_TX_TTL: U803.83 (IOR_119); also elsewhere on the board
/FPGA/GNDPLL0: C829.2, C830.2, U803.53 (GNDPLL0)
/FPGA/GNDPLL1: C827.2, C828.2, U803.127 (GNDPLL1)
/FPGA/VCCPLL0: C829.1, C830.1, R816.1, U803.54 (VCCPLL0)
/FPGA/VCCPLL1: C827.1, C828.1, R810.1, U803.126 (VCCPLL1)
/FPGA/iCE_CDONE: J802.5, R817.2, U803.65 (CDONE)
/FPGA/iCE_CRESET: J802.6, R812.1, R815.1, U803.66 (~CRESET)
/FPGA/iCE_MISO: J802.8, U803.67 (IOB_105_SDO), U809.5 (DQ0)
/FPGA/iCE_MOSI: J802.7, U803.68 (IOB_106_SDI), U809.2 (DQ1)
/FPGA/iCE_Rx_TTL: J802.3, U803.34 (IOL_25B)
/FPGA/iCE_SCK: J802.9, R818.2, U803.70 (IOB_107_SCK), U809.6 (C)
/FPGA/iCE_SS_B: J802.10, R819.2, U803.71 (IOB_108_SS), U809.1 (S#)
/FPGA/iCE_Tx_TTL: J802.4, U803.33 (IOL_25A)
AGNDF: C801.2, C802.2, C803.2, C804.2, C805.2, C806.2, C807.2, C808.2, C809.2, C810.2, C811.2, C812.2, C813.2, C814.2, C815.2, C816.2, C817.2, C818.2, C819.2, C820.2, C821.2, C822.2, C823.2, C824.2, C825.2, C826.2, D801.1 (K), D802.1 (K), J802.2, R815.2, U801.2 (GND), U801.5 (DIR), U802.2 (GND), U802.5 (DIR), U803.5 (GND), U803.13 (GND), U803.14 (GND), U803.59 (GND), U803.69 (GND), U803.86 (GND), U803.103 (GND), U803.132 (GND), U803.140 (GND), U804.2 (GND), U804.5 (DIR), U805.2 (GND), U805.5 (DIR), U806.2 (GND), U806.5 (DIR), U807.2 (GND), U808.2 (GND), U809.4 (VSS); also elsewhere on the board
unnamed: D801.2 (A), R807.2
unnamed: D802.2 (A), R809.2
unnamed: D803.1 (K), U803.108 (VPP_2V5)
unnamed: J801.1, U803.2 (IOL_2B)
unnamed: J801.2, U803.3 (IOL_3A)
unnamed: J801.3, U803.4 (IOL_3B)
unnamed: J801.4, U803.7 (IOL_4A)
unnamed: Q801.1 (B), R801.1
unnamed: R801.2, U803.1 (IOL_2A)
unnamed: R802.1, U803.110 (IOT_168)
unnamed: R803.1, U803.115 (IOT_172)
unnamed: R804.1, U803.121 (IOT_181)
unnamed: R805.1, U803.130 (IOT_206)
unnamed: R806.1, U803.136 (IOT_214)
unnamed: R807.1, U803.37 (IOB_56)
unnamed: R808.2, U807.5 (DIR)
unnamed: R809.1, U803.38 (IOB_57)
unnamed: R811.2, U808.3 (Out)
unnamed: R813.1, U809.3 (W#/DQ2)
unnamed: R814.1, U809.7 (DQ3/HOLD#)

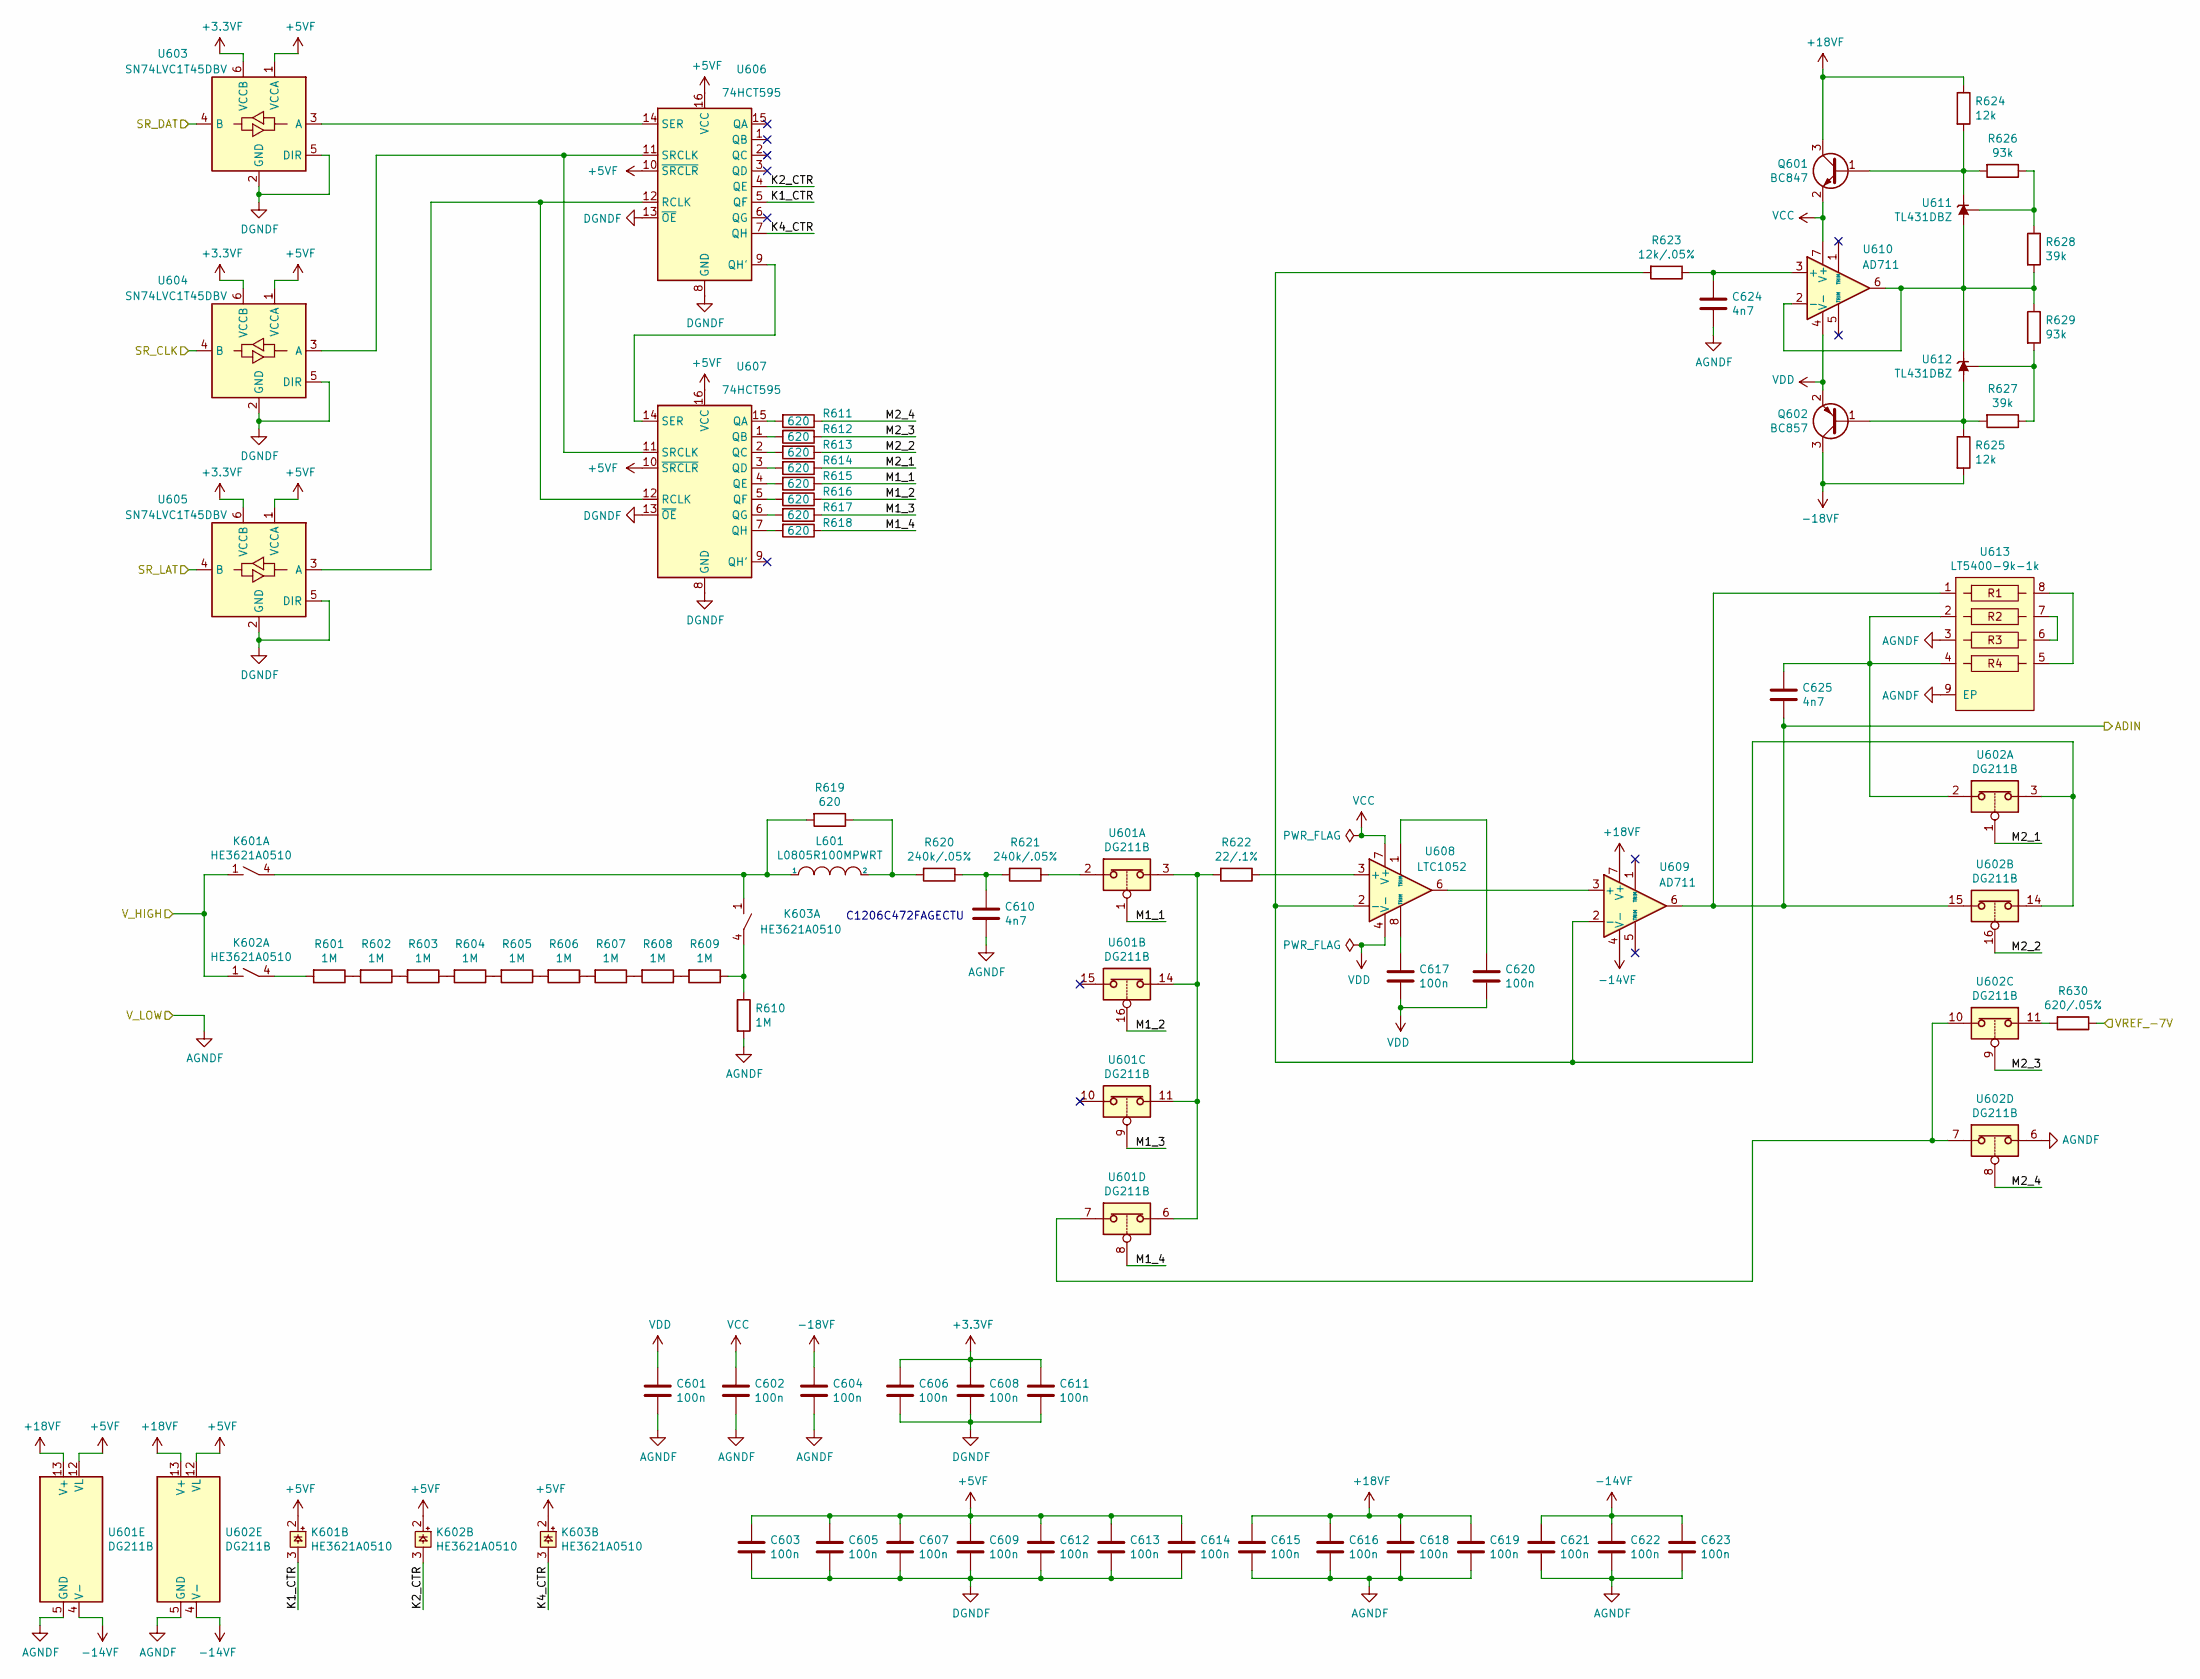
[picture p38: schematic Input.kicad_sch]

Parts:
C601, C602, C603, C604, C605, C606, C607, C608, C609, C611, C612, C613, C614, C615, C616, C617, C618, C619, C620, C621, C622, C623: 100n; C_0603_1608Metric_Pad1.05x0.95mm_HandSolder
C610: 4n7; C_1206_3216Metric_Pad1.42x1.75mm_HandSolder
C624, C625: 4n7; C_0603_1608Metric_Pad1.05x0.95mm_HandSolder
K601, K602, K603: HE3621A0510; HE360_x-5050462-8
L601: L0805R100MPWRT; R_0805_2012Metric_Pad1.15x1.40mm_HandSolder
Q601: BC847; SOT-23
Q602: BC857; SOT-23
R601, R602, R603, R604, R605, R606, R607, R608, R609, R610: 1M; R_0805_2012Metric_Pad1.15x1.40mm_HandSolder
R611, R612, R613, R614, R615, R616, R617, R618: 620; R_0603_1608Metric_Pad1.05x0.95mm_HandSolder
R619: 620; R_0805_2012Metric_Pad1.15x1.40mm_HandSolder
R620, R621: 240k/.05%; R_0805_2012Metric_Pad1.15x1.40mm_HandSolder
R622: 22/.1%; R_1206_3216Metric_Pad1.42x1.75mm_HandSolder
R623: 12k/.05%; R_0603_1608Metric_Pad1.05x0.95mm_HandSolder
R624, R625: 12k; R_0805_2012Metric_Pad1.15x1.40mm_HandSolder
R626, R629: 93k; R_0805_2012Metric_Pad1.15x1.40mm_HandSolder
R627, R628: 39k; R_0805_2012Metric_Pad1.15x1.40mm_HandSolder
R630: 620/.05%; R_0603_1608Metric_Pad1.05x0.95mm_HandSolder
U601, U602: DG211B; SOIC-16_3.9x9.9mm_P1.27mm
U603, U604, U605: SN74LVC1T45DBV; SOT-23-6
U606, U607: 74HCT595; TSSOP-16_4.4x5mm_P0.65mm
U608: LTC1052; DIP-8_W7.62mm_Socket
U609, U610: AD711; SOIC-8_3.9x4.9mm_P1.27mm
U611, U612: TL431DBZ; SOT-23
U613: LT5400-9k-1k; MSOP-8-1EP_3x3mm_P0.65mm_EP1.73x1.85mm_ThermalVias

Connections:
+3.3VF: C606.1, C608.1, C611.1, U603.6 (VCCB), U604.6 (VCCB), U605.6 (VCCB); also elsewhere on the board
+5VF: C603.1, C605.1, C607.1, C609.1, C612.1, C613.1, C614.1, K601.2, K602.2, K603.2, U601.12 (VL), U602.12 (VL), U603.1 (VCCA), U604.1 (VCCA), U605.1 (VCCA), U606.10 (~SRCLR), U606.16 (VCC), U607.10 (~SRCLR), U607.16 (VCC); also elsewhere on the board
+18VF: C615.1, C616.1, C618.1, C619.1, Q601.3 (C), R624.1, U601.13 (V+), U602.13 (V+), U609.7 (V+); also elsewhere on the board
-14VF: C621.1, C622.1, C623.1, U601.4 (V-), U602.4 (V-), U609.4 (V-); also elsewhere on the board
-18VF: C604.1, Q602.3 (C), R625.2; also elsewhere on the board
/ADC/ADIN: C625.2, U602.15, U609.6, U613.1; also elsewhere on the board
/ADC/VREF_-7V: R630.1; also elsewhere on the board
/Connector/V_HIGH: K601.1, K602.1; also elsewhere on the board
/Input/K1_CTR: K601.3, U606.5 (QF)
/Input/K2_CTR: K602.3, U606.4 (QE)
/Input/K4_CTR: K603.3, U606.7 (QH)
/Input/M1_1: R615.1, U601.1
/Input/M1_2: R616.1, U601.16
/Input/M1_3: R617.1, U601.9
/Input/M1_4: R618.1, U601.8
/Input/M2_1: R614.1, U602.1
/Input/M2_2: R613.1, U602.16
/Input/M2_3: R612.1, U602.9
/Input/M2_4: R611.1, U602.8
/Input/SR_CLK: U604.4 (B); also elsewhere on the board
/Input/SR_DAT: U603.4 (B); also elsewhere on the board
/Input/SR_LAT: U605.4 (B); also elsewhere on the board
AGNDF: C601.2, C602.2, C603.2, C604.2, C605.2, C606.2, C607.2, C608.2, C609.2, C610.1, C611.2, C612.2, C613.2, C614.2, C615.2, C616.2, C618.2, C619.2, C621.2, C622.2, C623.2, C624.2, R610.2, U601.5 (GND), U602.5 (GND), U602.6, U603.2 (GND), U603.5 (DIR), U604.2 (GND), U604.5 (DIR), U605.2 (GND), U605.5 (DIR), U606.8 (GND), U606.13 (~OE), U607.8 (GND), U607.13 (~OE), U613.3, U613.9 (EP); also elsewhere on the board
unnamed: C610.2, R620.1, R621.2
unnamed: C617.1, U608.8 (TRIM)
unnamed: C620.1, U608.1 (TRIM)
unnamed: C624.1, R623.1, U610.3 (+)
unnamed: C625.1, U602.2, U613.2, U613.4
unnamed: K601.4, K603.1, L601.1, R619.2
unnamed: K602.4, R601.2
unnamed: K603.4, R609.1, R610.1
unnamed: L601.2, R619.1, R620.2
unnamed: Q601.1 (B), R624.2, R626.2, U611.1 (K)
unnamed: Q602.1 (B), R625.1, R627.2, U612.3 (A)
unnamed: R601.1, R602.2
unnamed: R602.1, R603.2
unnamed: R603.1, R604.2
unnamed: R604.1, R605.2
unnamed: R605.1, R606.2
unnamed: R606.1, R607.2
unnamed: R607.1, R608.2
unnamed: R608.1, R609.2
unnamed: R611.2, U607.15 (QA)
unnamed: R612.2, U607.1 (QB)
unnamed: R613.2, U607.2 (QC)
unnamed: R614.2, U607.3 (QD)
unnamed: R615.2, U607.4 (QE)
unnamed: R616.2, U607.5 (QF)
unnamed: R617.2, U607.6 (QG)
unnamed: R618.2, U607.7 (QH)
unnamed: R621.1, U601.2
unnamed: R622.1, U608.3 (+)
unnamed: R622.2, U601.3, U601.6, U601.11, U601.14
unnamed: R623.2, U602.3, U602.14, U608.2 (-), U609.2 (-)
unnamed: R626.1, R628.1, U611.2 (REF)
unnamed: R627.1, R629.2, U612.2 (REF)
unnamed: R628.2, R629.1, U610.2 (-), U610.6, U611.3 (A), U612.1 (K)
unnamed: R630.2, U602.11
unnamed: U601.7, U602.7, U602.10
unnamed: U603.3 (A), U606.14 (SER)
unnamed: U604.3 (A), U606.11 (SRCLK), U607.11 (SRCLK)
unnamed: U605.3 (A), U606.12 (RCLK), U607.12 (RCLK)
unnamed: U606.9 (QH'), U607.14 (SER)
unnamed: U608.6, U609.3 (+)
unnamed: U613.5, U613.8
unnamed: U613.6, U613.7
VCC: C602.1, Q601.2 (E), U608.7 (V+), U610.7 (V+)
VDD: C601.1, C617.2, C620.2, Q602.2 (E), U608.4 (V-), U610.4 (V-)

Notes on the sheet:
C1206C472FAGECTU

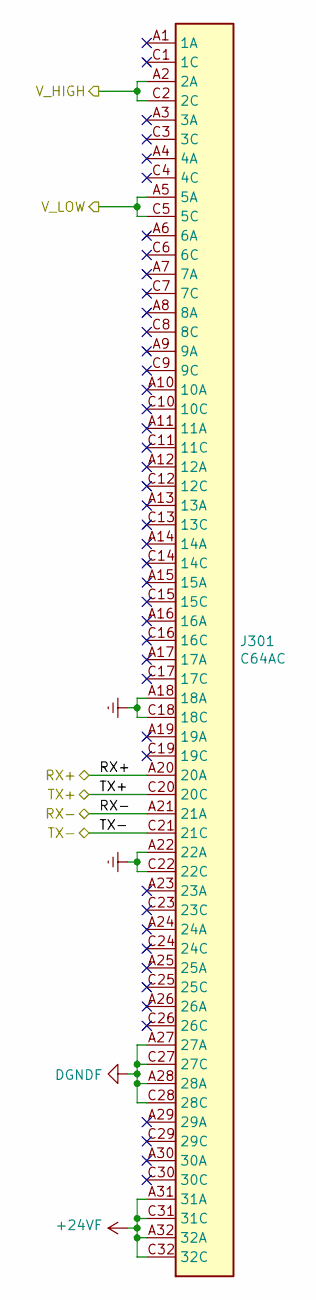
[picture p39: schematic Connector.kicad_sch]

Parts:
J301: C64AC; Socket_DIN41612-CaseC1-AC-Male-64Pin-2rows

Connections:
+24VF: J301.A31 (31A), J301.A32 (32A), J301.C31 (31C), J301.C32 (32C); also elsewhere on the board
/Connector/RX+: J301.A20 (20A); also elsewhere on the board
/Connector/RX-: J301.A21 (21A); also elsewhere on the board
/Connector/TX+: J301.C20 (20C); also elsewhere on the board
/Connector/TX-: J301.C21 (21C); also elsewhere on the board
/Connector/V_HIGH: J301.A2 (2A), J301.C2 (2C); also elsewhere on the board
AGNDF: J301.A5 (5A), J301.A27 (27A), J301.A28 (28A), J301.C5 (5C), J301.C27 (27C), J301.C28 (28C); also elsewhere on the board
Earth: J301.A18 (18A), J301.A22 (22A), J301.C18 (18C), J301.C22 (22C); also elsewhere on the board

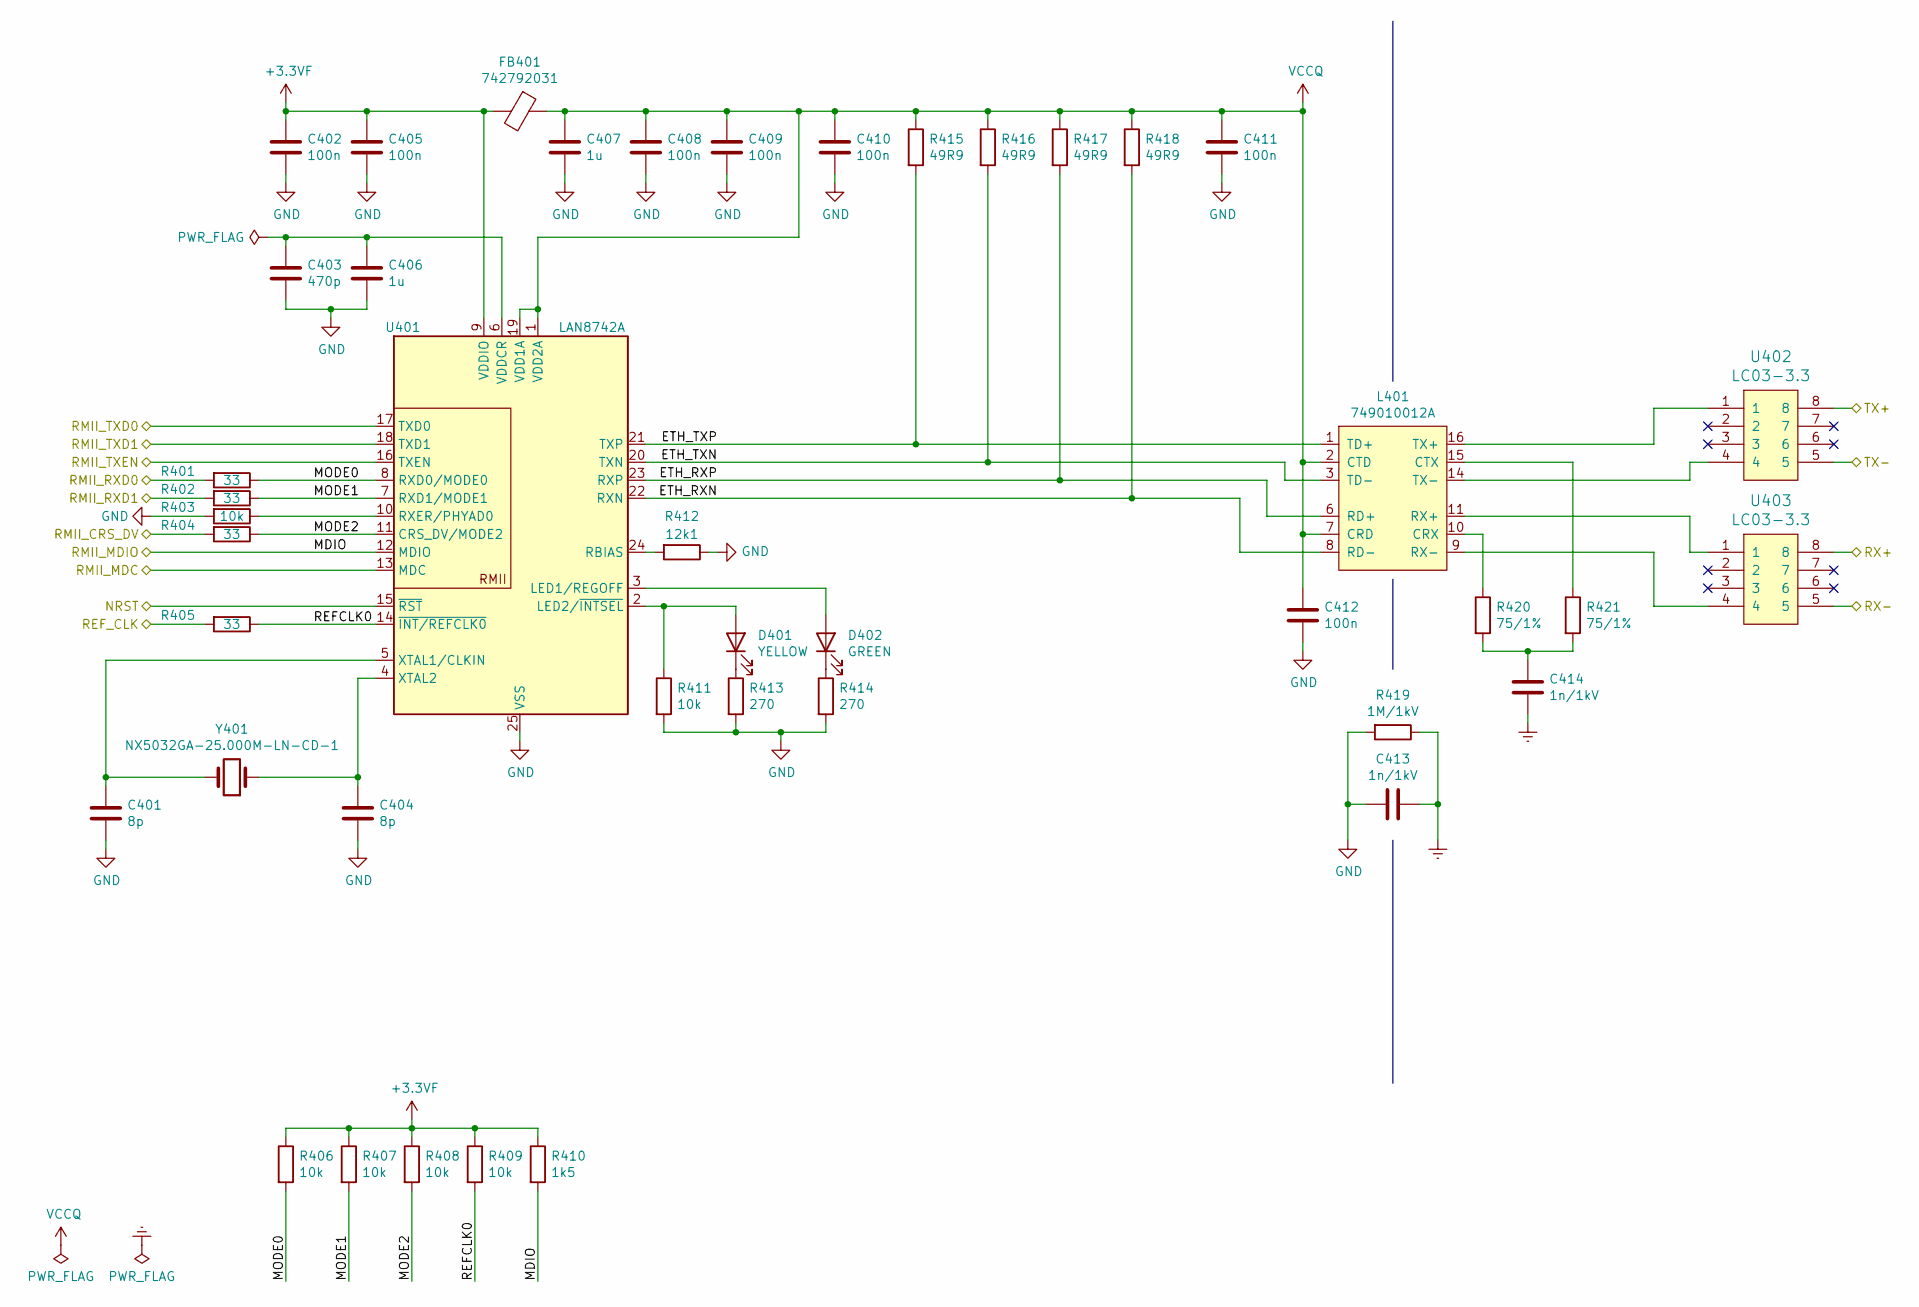
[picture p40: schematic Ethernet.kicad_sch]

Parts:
C401, C404: 8p; C_0603_1608Metric_Pad1.05x0.95mm_HandSolder
C402, C405, C408, C409, C410, C411, C412: 100n; C_0603_1608Metric_Pad1.05x0.95mm_HandSolder
C403: 470p; C_0603_1608Metric_Pad1.05x0.95mm_HandSolder
C406, C407: 1u; C_0603_1608Metric_Pad1.05x0.95mm_HandSolder
C413, C414: 1n/1kV; C_1206_3216Metric_Pad1.42x1.75mm_HandSolder
D401: YELLOW; LED_0603_1608Metric_Pad1.05x0.95mm_HandSolder
D402: GREEN; LED_0603_1608Metric_Pad1.05x0.95mm_HandSolder
FB401: 742792031; L_0805_2012Metric_Pad1.15x1.40mm_HandSolder
L401: 749010012A
R401, R402, R404, R405: 33; R_0603_1608Metric_Pad1.05x0.95mm_HandSolder
R403, R406, R407, R408, R409, R411: 10k; R_0603_1608Metric_Pad1.05x0.95mm_HandSolder
R410: 1k5; R_0603_1608Metric_Pad1.05x0.95mm_HandSolder
R412: 12k1; R_0603_1608Metric_Pad1.05x0.95mm_HandSolder
R413, R414: 270; R_0603_1608Metric_Pad1.05x0.95mm_HandSolder
R415, R416, R417, R418: 49R9; R_0603_1608Metric_Pad1.05x0.95mm_HandSolder
R419: 1M/1kV; R_1206_3216Metric_Pad1.42x1.75mm_HandSolder
R420, R421: 75/1%; R_0603_1608Metric_Pad1.05x0.95mm_HandSolder
U401: LAN8742A; QFN-24-1EP_4x4mm_P0.5mm_EP2.6x2.6mm_ThermalVias
U402, U403: LC03-3.3; SO8E
Y401: NX5032GA-25.000M-LN-CD-1; NX5032GA

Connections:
+3.3VF: C402.1, C405.1, FB401.2, R406.1, R407.1, R408.1, R409.1, R410.1, U401.9 (VDDIO); also elsewhere on the board
/Connector/RX+: U403.8; also elsewhere on the board
/Connector/RX-: U403.5; also elsewhere on the board
/Connector/TX+: U402.8; also elsewhere on the board
/Connector/TX-: U402.5; also elsewhere on the board
/Ethernet/ETH_RXN: L401.8 (RD-), R418.2, U401.22 (RXN)
/Ethernet/ETH_RXP: L401.6 (RD+), R417.2, U401.23 (RXP)
/Ethernet/ETH_TXN: L401.3 (TD-), R416.2, U401.20 (TXN)
/Ethernet/ETH_TXP: L401.1 (TD+), R415.2, U401.21 (TXP)
/Ethernet/MODE0: R401.1, R406.2, U401.8 (RXD0/MODE0)
/Ethernet/MODE1: R402.1, R407.2, U401.7 (RXD1/MODE1)
/Ethernet/MODE2: R404.1, R408.2, U401.11 (CRS_DV/MODE2)
/Ethernet/NRST: U401.15 (~RST); also elsewhere on the board
/Ethernet/REFCLK0: R405.1, R409.2, U401.14 (~INT/REFCLK0)
/Ethernet/REF_CLK: R405.2; also elsewhere on the board
/Ethernet/RMII_CRS_DV: R404.2; also elsewhere on the board
/Ethernet/RMII_MDC: U401.13 (MDC); also elsewhere on the board
/Ethernet/RMII_MDIO: R410.2, U401.12 (MDIO); also elsewhere on the board
/Ethernet/RMII_RXD0: R401.2; also elsewhere on the board
/Ethernet/RMII_RXD1: R402.2; also elsewhere on the board
/Ethernet/RMII_TXD0: U401.17 (TXD0); also elsewhere on the board
/Ethernet/RMII_TXD1: U401.18 (TXD1); also elsewhere on the board
/Ethernet/RMII_TXEN: U401.16 (TXEN); also elsewhere on the board
AGNDF: C401.2, C402.2, C403.2, C404.2, C405.2, C406.2, C407.2, C408.2, C409.2, C410.2, C411.2, C412.2, C413.2, R403.2, R411.2, R412.1, R413.2, R414.2, R419.2, U401.25 (VSS); also elsewhere on the board
Earth: C413.1, C414.2, R419.1; also elsewhere on the board
unnamed: C401.1, U401.5 (XTAL1/CLKIN), Y401.2
unnamed: C403.1, C406.1, U401.6 (VDDCR)
unnamed: C404.1, U401.4 (XTAL2), Y401.1
unnamed: C414.1, R420.2, R421.2
unnamed: D401.1 (K), R413.1
unnamed: D401.2 (A), R411.1, U401.2 (LED2/~INTSEL)
unnamed: D402.1 (K), R414.1
unnamed: D402.2 (A), U401.3 (LED1/REGOFF)
unnamed: L401.9 (RX-), U403.4
unnamed: L401.10 (CRX), R420.1
unnamed: L401.11 (RX+), U403.1
unnamed: L401.14 (TX-), U402.4
unnamed: L401.15 (CTX), R421.1
unnamed: L401.16 (TX+), U402.1
unnamed: R403.1, U401.10 (RXER/PHYAD0)
unnamed: R412.2, U401.24 (RBIAS)
VCCQ: C407.1, C408.1, C409.1, C410.1, C411.1, C412.1, FB401.1, L401.2 (CTD), L401.7 (CRD), R415.1, R416.1, R417.1, R418.1, U401.1 (VDD2A), U401.19 (VDD1A)

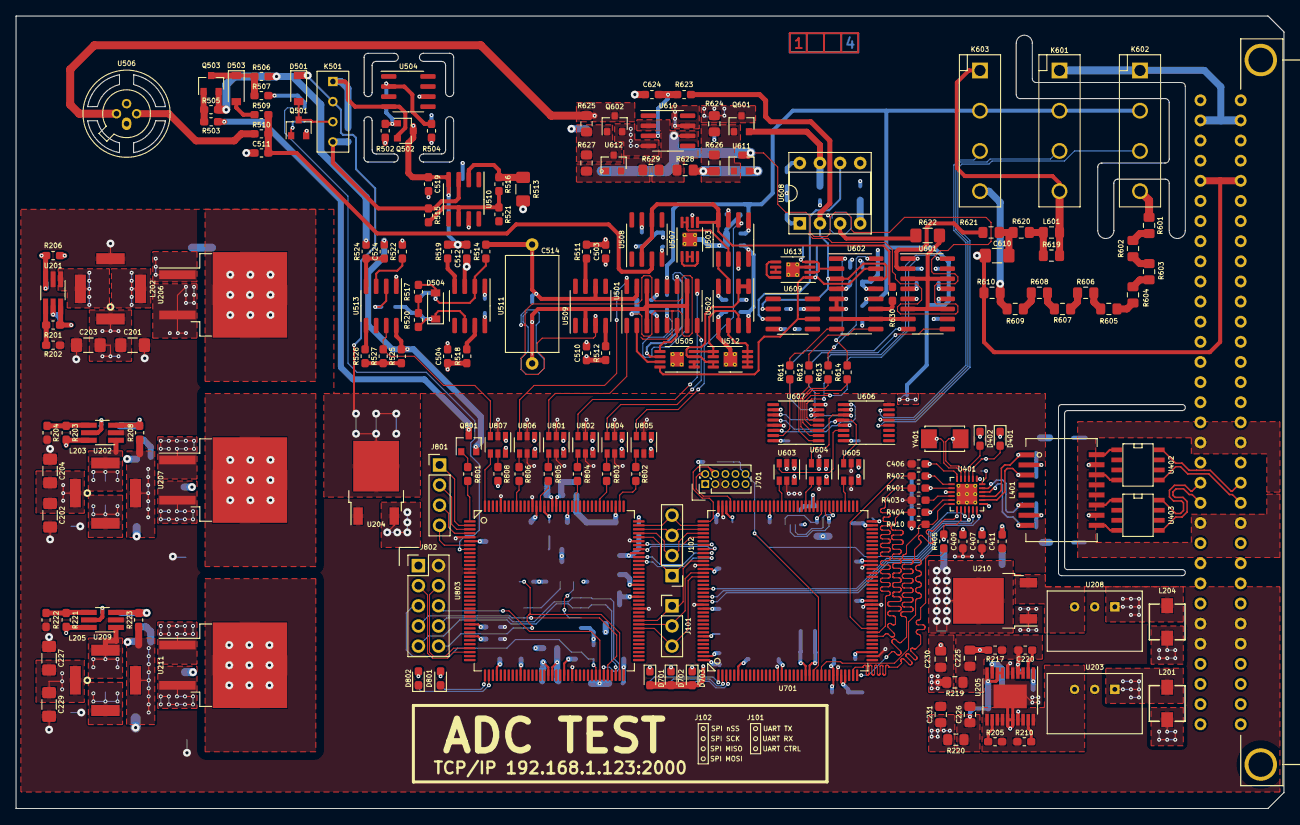
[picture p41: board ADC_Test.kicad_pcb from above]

Board: 4 copper layers, 160.0 x 100.0 mm, 383 parts (0 on the bottom side), 257 nets.

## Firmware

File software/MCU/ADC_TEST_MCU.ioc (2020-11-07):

#MicroXplorer Configuration settings - do not modify
ETH.IPParameters=MediaInterface,PHY_Name_RMII,PhyAddress
ETH.MediaInterface=ETH_MEDIA_INTERFACE_RMII
ETH.PHY_Name_RMII=LAN8742A_PHY_ADDRESS
ETH.PhyAddress=0
FREERTOS.FootprintOK=true
FREERTOS.IPParameters=Tasks01,configMINIMAL_STACK_SIZE,configTOTAL_HEAP_SIZE,configUSE_NEWLIB_REENTRANT,FootprintOK
FREERTOS.Tasks01=defaultTask,24,256,StartDefaultTask,Default,NULL,Dynamic,NULL,NULL;myTaskLED,8,256,StartTaskLED,Default,NULL,Dynamic,NULL,NULL;LogData,8,256,StartTaskLogData,Default,NULL,Dynamic,NULL,NULL
FREERTOS.configMINIMAL_STACK_SIZE=256
FREERTOS.configTOTAL_HEAP_SIZE=90720
FREERTOS.configUSE_NEWLIB_REENTRANT=1
File.Version=6
GPIO.groupedBy=Group By Peripherals
I2C4.IPParameters=Timing
I2C4.Timing=0x00C0EAFF
KeepUserPlacement=false
LWIP.DEFAULT_THREAD_STACKSIZE=2048
LWIP.GATEWAY_ADDRESS=192.168.000.001
LWIP.IPParameters=LWIP_DHCP,IP_ADDRESS,NETMASK_ADDRESS,GATEWAY_ADDRESS,MEM_SIZE,TCPIP_THREAD_STACKSIZE,DEFAULT_THREAD_STACKSIZE
LWIP.IP_ADDRESS=192.168.000.123
LWIP.LWIP_DHCP=0
LWIP.MEM_SIZE=6400
LWIP.NETMASK_ADDRESS=255.255.255.000
LWIP.TCPIP_THREAD_STACKSIZE=2048
LWIP.Version=v2.1.2_Cube
Mcu.Family=STM32F7
Mcu.IP0=CORTEX_M7
Mcu.IP1=ETH
Mcu.IP2=FREERTOS
Mcu.IP3=I2C4
Mcu.IP4=LWIP
Mcu.IP5=NVIC
Mcu.IP6=RCC
Mcu.IP7=SPI3
Mcu.IP8=SYS
Mcu.IP9=USART2
Mcu.IPNb=10
Mcu.Name=STM32F756ZGTx
Mcu.Package=LQFP144
Mcu.Pin0=PE2
Mcu.Pin1=PE3
Mcu.Pin10=PC5
Mcu.Pin11=PB15
Mcu.Pin12=PD11
Mcu.Pin13=PD12
Mcu.Pin14=PD13
Mcu.Pin15=PD15
Mcu.Pin16=PG7
Mcu.Pin17=PA13
Mcu.Pin18=PA14
Mcu.Pin19=PA15
Mcu.Pin2=PE4
Mcu.Pin20=PC10
Mcu.Pin21=PC11
Mcu.Pin22=PC12
Mcu.Pin23=PD1
Mcu.Pin24=PD2
Mcu.Pin25=PD3
Mcu.Pin26=PD4
Mcu.Pin27=PD5
Mcu.Pin28=PD6
Mcu.Pin29=PG11
Mcu.Pin3=PH0/OSC_IN
Mcu.Pin30=PG13
Mcu.Pin31=PG14
Mcu.Pin32=VP_FREERTOS_VS_CMSIS_V2
Mcu.Pin33=VP_LWIP_VS_Enabled
Mcu.Pin34=VP_SYS_VS_tim1
Mcu.Pin4=PH1/OSC_OUT
Mcu.Pin5=PC1
Mcu.Pin6=PA1
Mcu.Pin7=PA2
Mcu.Pin8=PA7
Mcu.Pin9=PC4
Mcu.PinsNb=35
Mcu.ThirdPartyNb=0
Mcu.UserConstants=
Mcu.UserName=STM32F756ZGTx
MxCube.Version=6.0.1
MxDb.Version=DB.6.0.0
NVIC.BusFault_IRQn=true\:0\:0\:false\:false\:true\:false\:false\:false
NVIC.DebugMonitor_IRQn=true\:0\:0\:false\:false\:true\:false\:false\:false
NVIC.ETH_IRQn=true\:5\:0\:true\:false\:true\:false\:false\:true
NVIC.ForceEnableDMAVector=true
NVIC.HardFault_IRQn=true\:0\:0\:false\:false\:true\:false\:false\:false
NVIC.MemoryManagement_IRQn=true\:0\:0\:false\:false\:true\:false\:false\:false
NVIC.NonMaskableInt_IRQn=true\:0\:0\:false\:false\:true\:false\:false\:false
NVIC.PendSV_IRQn=true\:0\:0\:false\:false\:false\:false\:false\:false
NVIC.PriorityGroup=NVIC_PRIORITYGROUP_4
NVIC.SVCall_IRQn=true\:0\:0\:false\:false\:false\:false\:false\:false
NVIC.SavedPendsvIrqHandlerGenerated=true
NVIC.SavedSvcallIrqHandlerGenerated=true
NVIC.SavedSystickIrqHandlerGenerated=true
NVIC.SysTick_IRQn=true\:0\:0\:false\:false\:false\:false\:false\:false
NVIC.TIM1_UP_TIM10_IRQn=true\:0\:0\:false\:false\:true\:false\:false\:true
NVIC.TimeBase=TIM1_UP_TIM10_IRQn
NVIC.TimeBaseIP=TIM1
NVIC.UsageFault_IRQn=true\:0\:0\:false\:false\:true\:false\:false\:false
PA1.Mode=RMII
PA1.Signal=ETH_REF_CLK
PA13.Mode=Serial_Wire
PA13.Signal=SYS_JTMS-SWDIO
PA14.Mode=Serial_Wire
PA14.Signal=SYS_JTCK-SWCLK
PA15.GPIOParameters=GPIO_Label
PA15.GPIO_Label=SP3_NSS
PA15.Locked=true
PA15.Signal=GPIO_Output
PA2.Mode=RMII
PA2.Signal=ETH_MDIO
PA7.Mode=RMII
PA7.Signal=ETH_CRS_DV
PB15.GPIOParameters=GPIO_Speed,GPIO_Label
PB15.GPIO_Label=SR_LAT
PB15.GPIO_Speed=GPIO_SPEED_FREQ_HIGH
PB15.Locked=true
PB15.Signal=GPIO_Output
PC1.Mode=RMII
PC1.Signal=ETH_MDC
PC10.Mode=Full_Duplex_Master
PC10.Signal=SPI3_SCK
PC11.Mode=Full_Duplex_Master
PC11.Signal=SPI3_MISO
PC12.Locked=true
PC12.Mode=Full_Duplex_Master
PC12.Signal=SPI3_MOSI
PC4.Mode=RMII
PC4.Signal=ETH_RXD0
PC5.Mode=RMII
PC5.Signal=ETH_RXD1
PD1.GPIOParameters=GPIO_Label
PD1.GPIO_Label=FPGA_IO3
PD1.Locked=true
PD1.Signal=GPIO_Output
PD11.GPIOParameters=GPIO_Label
PD11.GPIO_Label=EEPROM_WP
PD11.Locked=true
PD11.Signal=GPIO_Output
PD12.GPIOParameters=GPIO_Label
PD12.GPIO_Label=EEPROM_SCL
PD12.Locked=true
PD12.Mode=I2C
PD12.Signal=I2C4_SCL
PD13.GPIOParameters=GPIO_Label
PD13.GPIO_Label=EEPROM_SDA
PD13.Locked=true
PD13.Mode=I2C
PD13.Signal=I2C4_SDA
PD15.GPIOParameters=GPIO_Speed,GPIO_Label
PD15.GPIO_Label=SR_CLK
PD15.GPIO_Speed=GPIO_SPEED_FREQ_HIGH
PD15.Locked=true
PD15.Signal=GPIO_Output
PD2.GPIOParameters=GPIO_Label
PD2.GPIO_Label=FPGA_IO4
PD2.Locked=true
PD2.Signal=GPIO_Output
PD3.GPIOParameters=GPIO_Label
PD3.GPIO_Label=FPGA_IO1
PD3.Locked=true
PD3.Signal=GPIO_Output
PD4.GPIOParameters=GPIO_Label
PD4.GPIO_Label=FPGA_IO2
PD4.Locked=true
PD4.Signal=GPIO_Output
PD5.Mode=Asynchronous
PD5.Signal=USART2_TX
PD6.GPIOParameters=GPIO_Speed,GPIO_PuPd
PD6.GPIO_PuPd=GPIO_PULLUP
PD6.GPIO_Speed=GPIO_SPEED_FREQ_MEDIUM
PD6.Locked=true
PD6.Mode=Asynchronous
PD6.Signal=USART2_RX
PE2.GPIOParameters=GPIO_Speed,PinState,GPIO_Label
PE2.GPIO_Label=LED_RED
PE2.GPIO_Speed=GPIO_SPEED_FREQ_MEDIUM
PE2.Locked=true
PE2.PinState=GPIO_PIN_SET
PE2.Signal=GPIO_Output
PE3.GPIOParameters=GPIO_Speed,PinState,GPIO_Label
PE3.GPIO_Label=LED_GREEN
PE3.GPIO_Speed=GPIO_SPEED_FREQ_MEDIUM
PE3.Locked=true
PE3.PinState=GPIO_PIN_SET
PE3.Signal=GPIO_Output
PE4.GPIOParameters=GPIO_Speed,PinState,GPIO_Label
PE4.GPIO_Label=LED_BLUE
PE4.GPIO_Speed=GPIO_SPEED_FREQ_MEDIUM
PE4.Locked=true
PE4.PinState=GPIO_PIN_SET
PE4.Signal=GPIO_Output
PG11.Locked=true
PG11.Mode=RMII
PG11.Signal=ETH_TX_EN
PG13.Locked=true
PG13.Mode=RMII
PG13.Signal=ETH_TXD0
PG14.Locked=true
PG14.Mode=RMII
PG14.Signal=ETH_TXD1
PG7.GPIOParameters=GPIO_Speed,GPIO_Label
PG7.GPIO_Label=SR_DAT
PG7.GPIO_Speed=GPIO_SPEED_FREQ_HIGH
PG7.Locked=true
PG7.Signal=GPIO_Output
PH0/OSC_IN.Mode=HSE-External-Oscillator
PH0/OSC_IN.Signal=RCC_OSC_IN
PH1/OSC_OUT.Mode=HSE-External-Oscillator
PH1/OSC_OUT.Signal=RCC_OSC_OUT
PinOutPanel.RotationAngle=0
ProjectManager.AskForMigrate=true
ProjectManager.BackupPrevious=false
ProjectManager.CompilerOptimize=6
ProjectManager.ComputerToolchain=false
ProjectManager.CoupleFile=false
ProjectManager.CustomerFirmwarePackage=
ProjectManager.DefaultFWLocation=true
ProjectManager.DeletePrevious=true
ProjectManager.DeviceId=STM32F756ZGTx
ProjectManager.FirmwarePackage=STM32Cube FW_F7 V1.16.0
ProjectManager.FreePins=false
ProjectManager.HalAssertFull=false
ProjectManager.HeapSize=0x200
ProjectManager.KeepUserCode=true
ProjectManager.LastFirmware=true
ProjectManager.LibraryCopy=1
ProjectManager.MainLocation=Core/Src
ProjectManager.NoMain=false
ProjectManager.PreviousToolchain=
ProjectManager.ProjectBuild=false
ProjectManager.ProjectFileName=ADC_TEST_MCU.ioc
ProjectManager.ProjectName=ADC_TEST_MCU
ProjectManager.RegisterCallBack=
ProjectManager.StackSize=0x400
ProjectManager.TargetToolchain=STM32CubeIDE
ProjectManager.ToolChainLocation=
ProjectManager.UnderRoot=true
ProjectManager.functionlistsort=1-MX_GPIO_Init-GPIO-false-HAL-true,2-SystemClock_Config-RCC-false-HAL-false,3-MX_LWIP_Init-LWIP-false-HAL-false,4-MX_I2C4_Init-I2C4-false-HAL-true,5-MX_SPI3_Init-SPI3-false-HAL-true,6-MX_USART2_UART_Init-USART2-false-HAL-true,0-MX_CORTEX_M7_Init-CORTEX_M7-false-HAL-true
RCC.AHBFreq_Value=200000000
RCC.APB1CLKDivider=RCC_HCLK_DIV4
RCC.APB1Freq_Value=50000000
RCC.APB1TimFreq_Value=100000000
RCC.APB2CLKDivider=RCC_HCLK_DIV2
RCC.APB2Freq_Value=100000000
RCC.APB2TimFreq_Value=200000000
RCC.CECFreq_Value=32786.88524590164
RCC.CortexFreq_Value=200000000
RCC.EthernetFreq_Value=200000000
RCC.FCLKCortexFreq_Value=200000000
RCC.FamilyName=M
RCC.HCLKFreq_Value=200000000
RCC.HSE_VALUE=8000000
RCC.HSI_VALUE=16000000
RCC.I2C1Freq_Value=50000000
RCC.I2C2Freq_Value=50000000
RCC.I2C3Freq_Value=50000000
RCC.I2C4Freq_Value=50000000
RCC.I2SFreq_Value=192000000
RCC.IPParameters=AHBFreq_Value,APB1CLKDivider,APB1Freq_Value,APB1TimFreq_Value,APB2CLKDivider,APB2Freq_Value,APB2TimFreq_Value,CECFreq_Value,CortexFreq_Value,EthernetFreq_Value,FCLKCortexFreq_Value,FamilyName,HCLKFreq_Value,HSE_VALUE,HSI_VALUE,I2C1Freq_Value,I2C2Freq_Value,I2C3Freq_Value,I2C4Freq_Value,I2SFreq_Value,LCDTFToutputFreq_Value,LPTIM1Freq_Value,LSE_VALUE,LSI_VALUE,MCO2PinFreq_Value,PLLCLKFreq_Value,PLLI2SPCLKFreq_Value,PLLI2SQCLKFreq_Value,PLLI2SRCLKFreq_Value,PLLI2SRoutputFreq_Value,PLLM,PLLN,PLLQCLKFreq_Value,PLLQoutputFreq_Value,PLLSAIPCLKFreq_Value,PLLSAIQCLKFreq_Value,PLLSAIRCLKFreq_Value,PLLSAIoutputFreq_Value,PLLSourceVirtual,RNGFreq_Value,SAI1Freq_Value,SAI2Freq_Value,SDMMCFreq_Value,SPDIFRXFreq_Value,SYSCLKFreq_VALUE,SYSCLKSource,UART4Freq_Value,UART5Freq_Value,UART7Freq_Value,UART8Freq_Value,USART1Freq_Value,USART2Freq_Value,USART3Freq_Value,USART6Freq_Value,USBFreq_Value,VCOI2SOutputFreq_Value,VCOInputFreq_Value,VCOOutputFreq_Value,VCOSAIOutputFreq_Value
RCC.LCDTFToutputFreq_Value=96000000
RCC.LPTIM1Freq_Value=50000000
RCC.LSE_VALUE=32768
RCC.LSI_VALUE=32000
RCC.MCO2PinFreq_Value=200000000
RCC.PLLCLKFreq_Value=200000000
RCC.PLLI2SPCLKFreq_Value=192000000
RCC.PLLI2SQCLKFreq_Value=192000000
RCC.PLLI2SRCLKFreq_Value=192000000
RCC.PLLI2SRoutputFreq_Value=192000000
RCC.PLLM=4
RCC.PLLN=200
RCC.PLLQCLKFreq_Value=200000000
RCC.PLLQoutputFreq_Value=200000000
RCC.PLLSAIPCLKFreq_Value=192000000
RCC.PLLSAIQCLKFreq_Value=192000000
RCC.PLLSAIRCLKFreq_Value=192000000
RCC.PLLSAIoutputFreq_Value=192000000
RCC.PLLSourceVirtual=RCC_PLLSOURCE_HSE
RCC.RNGFreq_Value=200000000
RCC.SAI1Freq_Value=192000000
RCC.SAI2Freq_Value=192000000
RCC.SDMMCFreq_Value=200000000
RCC.SPDIFRXFreq_Value=192000000
RCC.SYSCLKFreq_VALUE=200000000
RCC.SYSCLKSource=RCC_SYSCLKSOURCE_PLLCLK
RCC.UART4Freq_Value=50000000
RCC.UART5Freq_Value=50000000
RCC.UART7Freq_Value=50000000
RCC.UART8Freq_Value=50000000
RCC.USART1Freq_Value=100000000
RCC.USART2Freq_Value=50000000
RCC.USART3Freq_Value=50000000
RCC.USART6Freq_Value=100000000
RCC.USBFreq_Value=200000000
RCC.VCOI2SOutputFreq_Value=384000000
RCC.VCOInputFreq_Value=2000000
RCC.VCOOutputFreq_Value=400000000
RCC.VCOSAIOutputFreq_Value=384000000
SPI3.CalculateBaudRate=25.0 MBits/s
SPI3.Direction=SPI_DIRECTION_2LINES
SPI3.IPParameters=VirtualType,Mode,Direction,CalculateBaudRate
SPI3.Mode=SPI_MODE_MASTER
SPI3.VirtualType=VM_MASTER
USART2.AutoBaudRateEnableParam=UART_ADVFEATURE_AUTOBAUDRATE_DISABLE
USART2.BaudRate=62500
USART2.DataInvertParam=ADVFEATURE_DATAINV_DISABLE
USART2.IPParameters=WordLength,VirtualMode-Asynchronous,AutoBaudRateEnableParam,MSBFirstParam,DataInvertParam,OverSampling,BaudRate
USART2.MSBFirstParam=ADVFEATURE_MSBFIRST_DISABLE
USART2.OverSampling=UART_OVERSAMPLING_16
USART2.VirtualMode-Asynchronous=VM_ASYNC
USART2.WordLength=WORDLENGTH_8B
VP_FREERTOS_VS_CMSIS_V2.Mode=CMSIS_V2
VP_FREERTOS_VS_CMSIS_V2.Signal=FREERTOS_VS_CMSIS_V2
VP_LWIP_VS_Enabled.Mode=Enabled
VP_LWIP_VS_Enabled.Signal=LWIP_VS_Enabled
VP_SYS_VS_tim1.Mode=TIM1
VP_SYS_VS_tim1.Signal=SYS_VS_tim1
board=custom
isbadioc=false

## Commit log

2020-10-08 Schematic design.
    [ADC.sch, ADC_Test.sch, Connector.sch, Ethernet.sch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]
2020-10-08 Calculated voltages for the voltage sources.
    [Power.sch]
2020-10-08 Replaced TL061 with AD711.
    [Input.sch]
2020-10-08 Schematic, PCB and BOM.
    [ADC.sch, ADC_Test.csv, ADC_Test.ods, ADC_Test.sch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]
2020-10-09 Changes in documentation, schematics and PCB.
    [ADC.sch, ADC_Test.kicad_pcb, ADC_Test.sch, Connector.sch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]
2020-10-11 PCB design
    [ADC.sch, ADC_Test.kicad_pcb, ADC_Test.sch, Connector.sch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]
2020-10-11 PCB design.
    [ADC.sch, ADC_Test.kicad_pcb, ADC_Test.sch, FPGA.sch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]
2020-10-12 PCB layout almost done.
    [ADC_Test.kicad_pcb]
2020-10-12 PCB design done.
    [ADC.sch, ADC_Test.kicad_pcb, ADC_Test.sch, ADC_Test_Add.ods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]
2020-10-13 Added STM32 project.
    [ADC_Test_Add.ods]
2020-11-03 MCU readout from FPGA works.
    [ADC_Test.kicad_pcb, Input.sch]
2020-11-08 MCU sofware development.
    [ADC_Test.kicad_pcb]
2020-11-09 Modified the measurement functions. PCB ready for calibration.
2020-11-10 Calibrated ADC with a Inmel 7000 calibrator. Gain and offset values are in main.h.
2024-07-05 Updated hardware design to KiCAD 8.0. Stared to create the readme.md file
    [ADC.kicad_sch, ADC_Test.kicad_sch, Connector.kicad_sch, Ethernet.kicad_sch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]
